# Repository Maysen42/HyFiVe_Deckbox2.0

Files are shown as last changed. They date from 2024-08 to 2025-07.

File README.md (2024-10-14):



# HyFiVe - Hydrography on Fishing Vessels

<figure> 
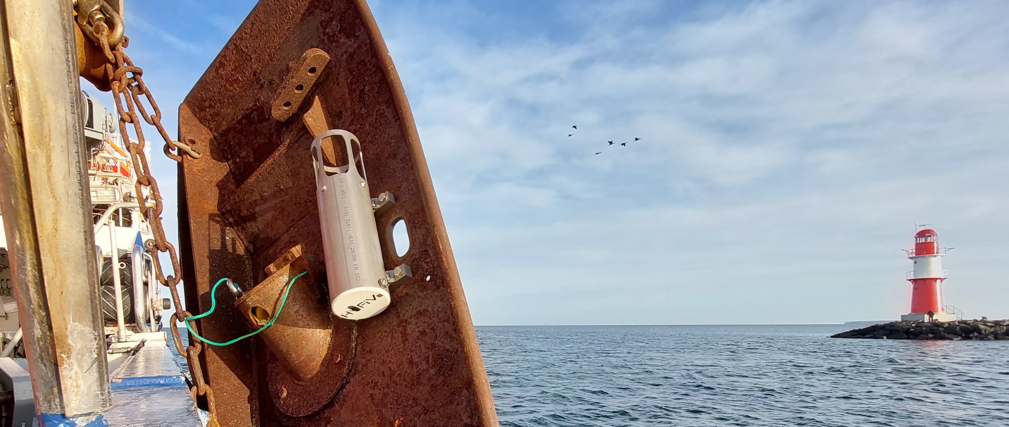
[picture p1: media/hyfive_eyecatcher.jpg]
hyfive_eyecatcher
   
</figure>

## Project Background 
Whether for modelling climate change or for our understanding of fish stocks – ocean data is essential for many disciplines. Usually, this data is collected by research vessels, which are cost-intensive and thus limited in space and time. To increase data resolution ‘vessels of opportunity’ can be a scalable alternative. In this concept vessels are used as measuring platforms, that are originally financed for a non-scientific purpose. Especially fishing vessels are of interest as they deploy gear in deep water and so make the whole water column accessible for an attached measuring system.

For this use case we developed a very flexible autonomous measuring system, which can be deployed on fishing gear to collect data in an affordable and scalable way. This was done within the **project ‘Hydrography on Fishing Vessels - HyFiVe’**
- Project period: Sept 2021 until Sept 2024
- Project partners:  
    - Thünen-Institute of Baltic Sea Fisheries (TIOF), Rostock, Germany, [https://www.thuenen.de/en/institutes/baltic-sea-fisheries/projects/fisheries-and-survey-technology/hyfive-hydrography-on-fishing-vessels](https://www.thuenen.de/en/institutes/baltic-sea-fisheries/projects/fisheries-and-survey-technology/hyfive-hydrography-on-fishing-vessels)
    - Leibnitz-Institute for Baltic Sea Research Warnemünde (IOW), Germany [https://www.io-warnemuende.de/project/278/hyfive.html](https://www.io-warnemuende.de/project/278/hyfive.html)
    - Hensel Elektronik GmbH, Rostock, Germany [https://hensel-elektronik.de](https://hensel-elektronik.de)
- Project webpage: hyfive.info
- Contact: See hyfive.info

## The HyFiVe System

This measuring system essentially consists of three components: 
- [01 Logger](./01_Logger/): Measures data with implemented OEM sensors while in the water and transmits them wireless afterwards.
- [02 Deck box](./02_Deckbox/): Receives measuring data via wifi, geo-references and stores it, visualizes it locally via webservice and transmits it to shore. The deck box also forwards config updates from server to loggers.
- [03 Land-Based Server](./03_Server/): Central infrastructure with a relational database, a configuration interface for remote maintenance and a tool for visualization of measuring data.

As overarching topic, [bi-directional communication](./bi_directional_communication/) between these components is described separately. 

The HyFiVe system offers many advantages:
- Autonomous operation up to several month
- Usable for non-experts, robust design
- Affordable price 
- Near live transmission of geo-referenced data to shore
- Scalability: Designed for a growing fleet of loggers and deck boxes
- Flexibility: Tested in various use cases, e.g. on trawl nets, as handheld probe and on sailing vessels 
- Modular design of logger facilitating easy change of sensors and integration of new ones
- Bi-directional data flow offering possibilities for remote servicing (VPN to deck box, config.json file for logger) 
- Comprehensive meta data
- Use of open sub-components and open standards lowering costs and facilitating reuse (e.g. ESP32, Raspberry Pi, nodeRed, InfluxDB, netcdf, https://cfconventions.org/ for naming variables)
- Open source, so you can modify and commercialise (according to the licenses below)

The system was developed in an agile method, so prototypes were built from an early stage on and tested continuously. Till the end of the first project in Sept 2024 the system was deployed on over ten vessels, among them research vessels, trawl fishing vessels, gill net fishing vessels and recreational vessels like sailing boats. 

<figure> 
   system_overview

   <figurecaption><a name="figure1">*Figure 1:*</a> *Logger, deck box and server - the three components of the HyFiVe measuring system*</figurecaption>
</figure>

## Github Repository
This documentation is aimed to enable you to build an own HyFiVe system and therefore contains detailed informations about all parts. If you are interested in building a system and lack information, please get in contact with us. 

**Disclaimer: We do not guarantee that the description is accurate throughout or complete. All your work is done at your own risk. Please comply with all necessary and legal safety precautions, especially when high voltage is involved, to avoid damage to yourself, others and the hardware.**

The three components have separate folders with hardware, software and specific information including READMEs which can be followed step by step. The READMEs contain
- Purpose and short description
- Used tools (hardware and software)
- Bills of Materials
- Additional information in the making/deploying

## Licenses
HyFiVe is an open-source project consisting of software, hardware, and documentation components. Each part of this project is licensed under a different copyleft license to ensure it remains free and open:

- Software/Code is licensed under [MPL-2.0](LICENSE_MPL-2.0)
- Hardware is licensed under [CERN-OHL-W-2.0 or later](LICENSE_CERN-OHL-W-2.0)
- Documentation is licensed under [CC-BY-SA-4.0](LICENSE_CC-BY-SA-4.0)

The HyFiVe logo is not published under above licenses and not free to use. 

An overview of the legal implications resulting from this licenses can be fund under [https://joinup.ec.europa.eu/collection/eupl/solution/joinup-licensing-assistant/jla-find-and-compare-software-licenses](https://joinup.ec.europa.eu/collection/eupl/solution/joinup-licensing-assistant/jla-find-and-compare-software-licenses).

## Funding
This project was funded by the German Federal Ministry of Food and Agriculture. 
<figure> 
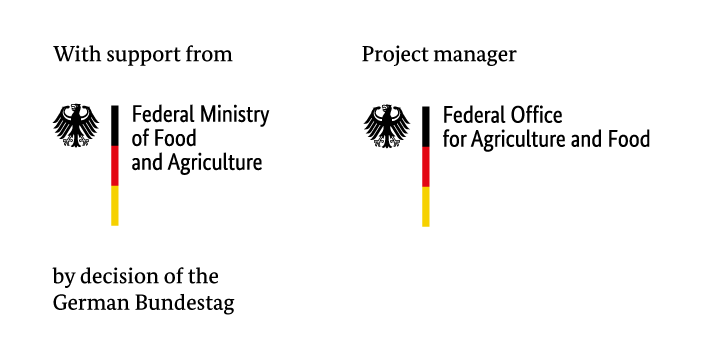
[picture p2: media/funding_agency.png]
funding_agency
   
</figure>

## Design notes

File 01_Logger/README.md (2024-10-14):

# Logger

The HyFiVe logger is an autonomous measuring unit, which can be attached to fishing gear. It consists of a pressure housing, internal electronics and firmware as well as sensors. 

Sensors: We integrate third-party (OEM) sensors. We are not limited to specific measurement parameters or manufactures. Many different sensors can be integrated, so the system can be adapted to your use case. So far we implemented and tested thoroughly sensors for conductivity, temperature, pressure (CTD) and oxygen.

Measurement process: The logger checks regularly if it is immersed into water. When the beginning of a deployment is detected, the state of logger is changed and it starts measuring with a prescribed period. When the logger is above the water surface again, this is also detected and the logger transmits the data via Wifi MQTT to the deck box. 

Config update: The configuration of the logger can be changed by altering config parameters, which are contained in a config.json file. The logger tries in regular intervals (which are also a config parameter) to connect to the deck box and asks, if a new config is available for it. If so, it is transmitted via Wifi MQTT.

## Different Versions of HyFiVe Loggers

We developed two versions of HyFiVe loggers. The HyFiVe deck box and the server do not need to be adapted to the logger version, they work with both.

There is no significant difference between the two versions regarding: 
- Mechanics (Only one end cap and the internal mountings are different)
- Sensors

The main differences between both versions are explained below. Both versions are explained in detail in the corresponding subfolders. 

### Basic Logger
The [basic logger](./01_Basic_Logger/) was developed by building prototypes from an early stage on (agile development). The prototypes were deployed in field tests and the results used to improve the design. Until the end of the first HyFiVe project in Sept 2024, all measuring campaigns on more than 10 vessels were conducted with this logger version. 

The electronic design is straight forward and easier to reproduce than the modular logger. It is based on only one PCB. All sensors are directly interfaced to micro controller on the PCB. 

<figure> 
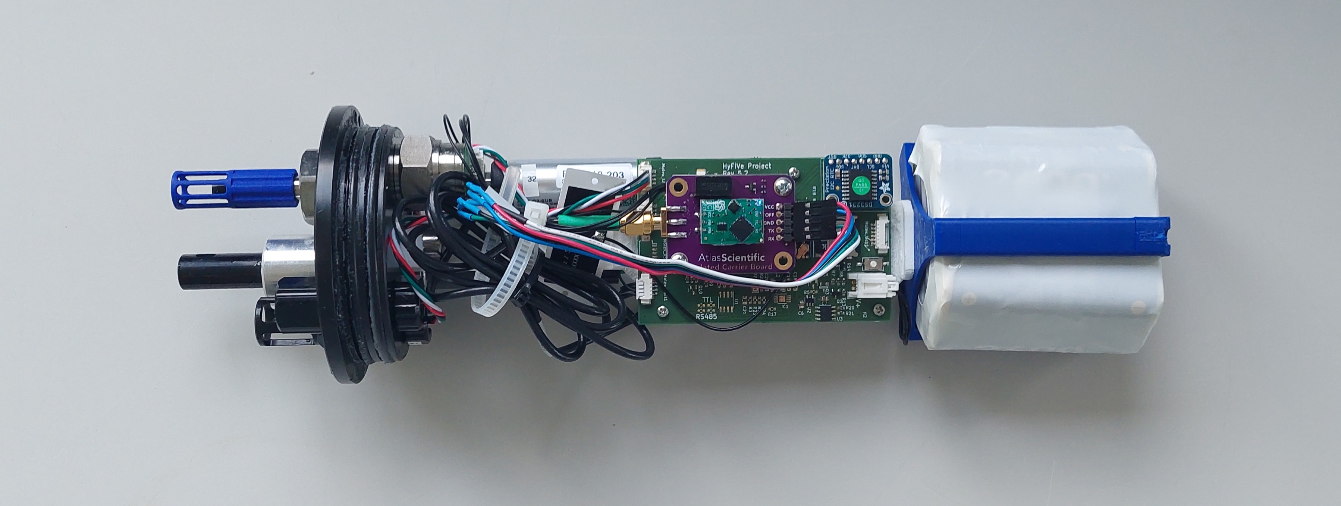
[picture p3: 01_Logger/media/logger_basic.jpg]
basic_logger
   

   <figurecaption><a name="figure1">*Figure 1:*</a> *Electronics of basic logger*</figurecaption>
</figure>

### Modular Logger
The [modular logger](./02_Modular_Logger/) offers more functionalities and it's design is more complex. The development took more time, so the prototypes could only be tested in harbour tests until the end of the first HyFiVe project in Sept 2024. 

The modularity is the main difference between both versions: In the modular logger each sensor is connected to one interface PCB. All interface PCBs are connected to a main PCB. The communication between main PCB and interface PCB is standardized. In this way, all sensor specific things can be encapsulated on the interface PCB.

In comparison to the basic version, the modular logger offers the following additional features: 
 - Modular design facilitates integrating and changing sensors, s. above.
 - Battery management
 - Charging of batteries without opening pressure case 
 - LED for feedback
 - Magnetic switch, e.g. for resetting the logger
 - Easier update of logger configuration: Manual trigger of update with magnet possible, more config parameters available, more precautions taken for stable config update
 - Error Log
 - Special operation modes possible: Change of sample rate for single sensors or during down- and upcast
 
<figure> 
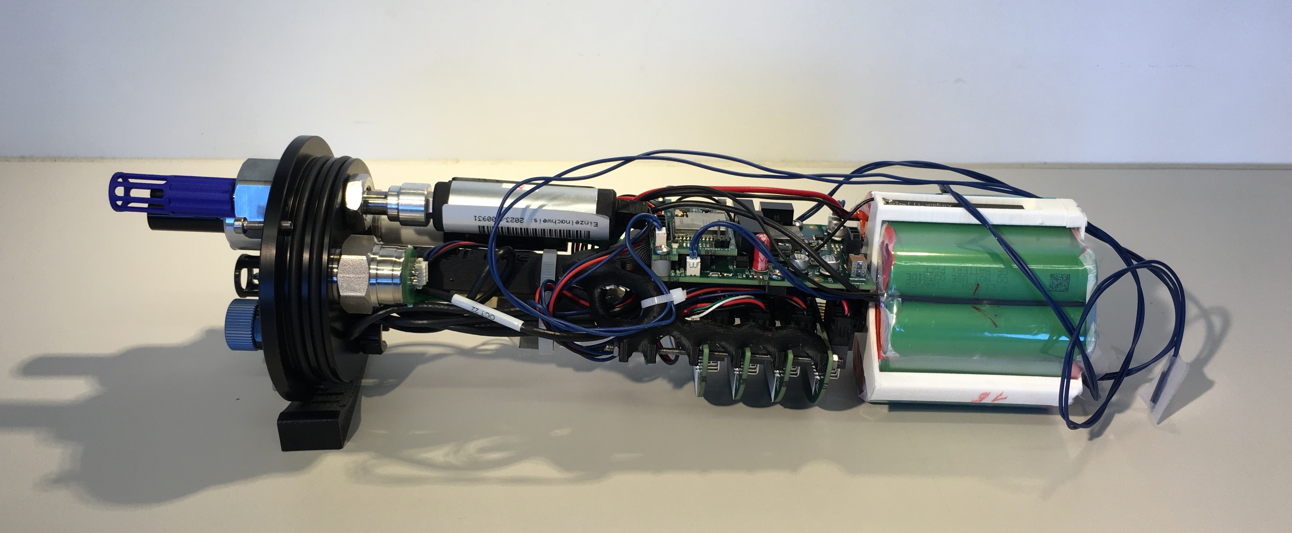
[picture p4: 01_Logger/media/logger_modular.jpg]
modular_logger
   

   <figurecaption><a name="figure2">*Figure 2:*</a> *Electronics of modular logger*</figurecaption>
</figure>

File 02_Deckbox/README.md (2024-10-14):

# Deck box

<figure> 
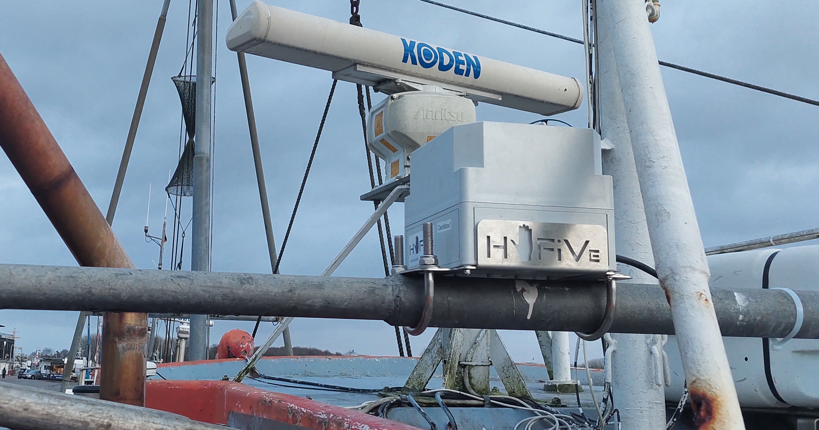
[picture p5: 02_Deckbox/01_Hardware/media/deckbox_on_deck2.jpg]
deckbox_on_deck
   

   <figurecaption><a name="figure1">*Figure 1:*</a> *Deck box installed on mast of fishing vessel using steel mounting*</figurecaption>
</figure>

## Main Components

The main hardware components of the deck box are:
- Router RUT955 by Teltonika
- Raspberry Pi 4B
- power supply and antennas
- waterproof case incl. internal and external mounting

## Main Functionalities 
The router provides:
- Wifi incl. MQTT broker for communication to the logger
- Mobile internet connection for communication to server
- GPS, published as NMEA string
- NTP server for time update of logger
- VPN client incl. port forwarding to Pi for remote servicing of deck box

The Raspberry Pi runs the main functionalities of the deck box:
- InfluxDB: Timeseries database for storing measuring data locally and buffering GPS data
- NodeRED: Handling all data flows:
    - measuring data is received via MQTT, merged with GPS data and stored locally
    - measuring data is saved as netCDF file and send to server in regular intervals
    - status files are received from loggers and forwarded to server
    - config files are downloaded from server in regular intervals
    - config files are send via MQTT, if requested by logger (incl. writing an error log)
- Grafana: Webinterface available for crew on board to visualize measuring data offline
- Self developed visualization webinterface (by a student): Installation is described, but files not contained in this repo, see [https://github.com/TreeM4n/HyFiVe](https://github.com/TreeM4n/HyFiVe)
- Docker and Portainer: Used for encapsuling above software

## Instructions

To build and configure a deck box follow the instructions in the following chapters:
1. [**Hardware:**](./01_Hardware/) Description of the mechanic and electric hardware incl. Bills of Material.
2. [**Software:**](./02_Software/) Description of the software setup.

<figure> 
   whole_deckbox_named

   <figurecaption><a name="figure2">*Figure 2:*</a> *Look inside a deck box*</figurecaption>
</figure>

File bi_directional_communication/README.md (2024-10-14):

# Bi-directional Communication between Server and Logger

## Data Flow from Logger to Server

<figure> 
   Data_flow_logger2land

   <figurecaption><a name="figure1">*Figure 1:*</a> *Data flow from logger to land*</figurecaption>
</figure>

The following data flow on the server is described in [../03_Server](../03_Server/)

This flow consists mainly of **measuring data**:
1. After a deployment, the logger tries to connect with the Wifi and send the data via MQTT
2. On the deck box in  NodeRED the data is merged with buffered GPS info and saved locally to the Influx database.
3. In regular intervals NodeRED triggers a python script, which aggregates new deployments into netCDF files, and sends them via sftp to the server (mailbox/in/netcdf/logger_ID/).
4. On the server, the measuring data is quality checked and saved in the relational data base
5. The measuring data is forwarded to other data bases via interfaces and can be visualised on our own [web interface](../03_Server/04_Webinterfaces/) under hyfive.info:4001

In addition each logger sends **status information**:
1. Each logger sends in regular intervals (which is a config parameter) it's battery and memory status via Wifi/MQTT.
2. On the deck box in NodeRED this information is merged with the current position of the deck box and saved as a status.json file
3. This file is sent via mobile network and sftp to the server (mailbox/in/status/logger_ID/). Example file: [logger_17_status_1724931613709.json](./logger_17_status_1724931613709.json)
4. The information is shown in the config [interface](../03_Server/04_Webinterfaces/).

## Data Flow from Server to Logger

<figure> 
   Data_flow_land2logger

   <figurecaption><a name="figure2">*Figure 2:*</a> *Data flow from land to logger*</figurecaption>
</figure>

An aim of the HyFiVe project is, that a fleet of measuring systems can be managed with small effort. Therefore we developed a ways of remote servicing.

A comprehensive way for remote servicing the deck box, is to connect to it via VPN. The expert user onshore can configure both main components, the router (via it's webinterface) and Raspberry Pi (via SSH). Also all software interfaces like NodeRED and InfluxDB can be reached via port forwarding. 

For changing the configuration of loggers, which are already deployed on a remote vessel, we defined a set of config parameters, which are stored in a config.json file.

The **config files** can be created with an [web interface](../03_Server/04_Webinterfaces/) on the server and handed down from server to loggers:
1. Creation:  
After creation by the webinterface, the config files are stored on the server:
    - location: mailbox/out/config/logger_ID/
    - file name: logger_ID_config_DATE, with DATE like YYYYMMDDHHMM, e.g. logger_10_config_202405071357
The format of the file name is important and shall not be altered, as the ID in the file name is used to them assign to the right logger and the date is used to identify the latest file. 
2. Transmission from server to deck box:   
Each deck box copies all config files from the server to a local repository. This is done in regular intervals by a flow in NodeRED on the deck box. 
3. Transmission from deck box to logger:  
As a deck box does not know which loggers are close and also has no way (implemented) to start a MQTT connection, the loggers need to ask for updates. They do this in regular intervals given by the config parameter config_update_periode. The process is described in detail below. 

More info on config parameters and their transmission is given in [./01_config_update/](./01_config_update/).

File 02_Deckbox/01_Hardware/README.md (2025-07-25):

# Bill of material

The following parts are needed to manufacture a HyFiVe deckbox.

| #   | Amount | Unit | Name                                                                                                                        | GTIN                                  |
| --- | ------ | ---- | --------------------------------------------------------------------------------------------------------------------------- | ------------------------------------- |
|     |        |      | **Electronic components**                                                                                                   |                                       |
| 1   | 1      | pc   | Raspberry Pi 4 B 4GB ram , incl. Micro SD card (min 8 GB) and official case                                                 | 0765756931182  644824914923           |
| 2   | 1      | pc   | Router Teltonika RUT955 incl. supplied antennas (2 x wifi, 2 x mobile data, 1 x GPS)                                        | 4779027311302                         |
| 3   | 1      | pc   | Sim card incl. mobile data                                                                                                  |                                       |
| 4   | 1      | pc   | Network cable, short, small bending radius (e.g. 0.2 m)                                                                     | e.g. 4052792024371                    |
|     |        |      | **Internal power supply**                                                                                                   |                                       |
| 5   | 1      | pc   | Self designed PCB  for power distribution incl. fuse and diodes, see (TODO **LINK TO SCHEMATICS**)                          | self manufactured                     |
| 6   | 1      | pc   | ACDC converter, 12 or 24 V output, min 20 W, e.g. Mean Well LPV-20-12 LED Trafo                                             | 4021087006965                         |
| 7   | 1      | pc   | DCDC Converter, Input 8-58V, output: 5V, max. 15 W, e.g. K480503                                                            | 8852090466622                         |
| 8   | 1      | pc   | power plug for RUT955, either cut and reused from ACDC unit                                                                 |                                       |
| 9   | 1      | pc   | alternativly: Molex crimp socket 'Micro-Fit' 2x2-poles plus 4 x crimp contact  2824-20                                      | product numbers 0039039042 430300038  |
| 10  | 2      | pc   | 2-core wire ~25 cm, 2 x ~0.5mm², red and black                                                                              | 4040849567070                         |
| 11  | 6      | pc   | electric wire ferrule 0.5mm² 												    | 9900000247027			    |
| 12  | 4      | pc   | Heat shrink tubing 20mm x 3mm 												    | 9900000174064			    |
| 13  | 1      | pc   | USB-C Plug, e.g. recable USB C to C plug 5 strands set (consits of 3 parts: plug, housing and heat shrink tubing)           |		  	                    |
|     |        |      | **External power supply**                                                                                                   |                                       |
| 14  | 1      | pc   | Power cable, ~15 m, 2 wires, ~1mm², suited for outdoor/deck                                                                 | 2050005621999                         |
|     |        |      | **For connection to 230  V**                                                                                                |                                       |
| 15  | 1      | pc   | Socket Weipu SP2212/P3-1N, male, 3 pins, IP68                                                                               | 2050001515001                         |
| 16  | 1      | pc   | Plug Weipu SP2110 / S 3 I, female, 3 pins, IP68                                                                             | 2050001514738                         |
| 17  | 1      | pc   | Cover Weipu SP2110-Cap                                                                                                      | 2050001515353                         |
| 18  | 1      | pc   | Cover Weipu SP2111-Cap                                                                                                      | 2050001515360                         |
| 19  | 1      | pc   | Protected contact plug (Schuko) for connection to 230 V grid                                                                | 4011160604126                         |
|     |        |      | **For connection to 12/24 V**                                                                                               |                                       |
| 20  | 1      | pc   | Socket Weipu SP2212/P2-1N, male, 2 pins, IP68                                                                               | 2050001514998                         |
| 21  | 1      | pc   | Plug Weipu SP2110 / S 2 I, female, 2 pins, IP68                                                                             | 2050001514721                         |
| 22  | 1      | pc   | Cover Weipu SP2110-Cap                                                                                                      | 2050001515353                         |
| 23  | 1      | pc   | Cover Weipu SP2111-Cap                                                                                                      | 2050001515360                         |
| 24  | 1      | pc   | Plug of your coice for connection to low voltage grid                                                                       |                                       |
|     |        |      | **Case incl. internal mountings**                                                                                           |                                       |
| 25  | 1      | pc   | FIBOX Case 180x180x150 (Product-No.: 6011323)                                                                               | 6418074052216                         |
| 26  | 1      | pc   | 3D printed mounting for electronic components, consisting of four parts TODO **Link to STEP files**                         | self manufactured                     |
| 27  | 1      | pc   | 3D printed mounting for antennas of RUT955, consisting of three layers<br>TODO **Link to STEP files**                       | self manufactured                     |
| 28  | 4      | pc   | Threaded inserts to melt into 3D print, M3x5x4                                                                              | e.g. ASIN B09B7F2XM3 or 4260528721160 |
| 29  | 4      | pc   | Allen screws M3x16                                                                                                          | 4043952175507                         |
| 30  | 2      | pc   | Cable ties small                                                                                                            | 9900000247645                         |
| 31  | 2      | pc   | Tapping screw 2.2 x 6.5                                                                                                     | 4043377162199                         |
| 32  | 28     | pc   | Tapping screw 2.9 x 9.5                                                                                                     | 4043952537589                         |
| 33  | 4      | pc   | Tapping screw 3.9 x 9.5                                                                                                     | 4043377159625                         |
| 34  | 4      | pc   | (plastic) washers for 3.9 mm with large outer diameter                                                                      | 4043952665589 or 4001796381737        |
| 35  | 1      | pc   | ~5 cm foam tape (20 x 2 mm)                                                                                                 | 4260396830346                         |
|     |        |      | **Mounting for box on reeling**                                                                                             |                                       |
| 36  | 1      | pc   | Mounting plate, watercutted, stainless steel V4A<br>TODO **Link to STEP files**                                             | self manufactured                     |
| 37  | 4      | pc   | Allen screw, M4x16, incl. washer and self-securing nut, stainless steel V4A                                                 | 4043377065032			    |
| 38  | 2      | pc   | Steel strap for tubes, DIN 3570, nominal width 46 mm, incl. 2 M10 self-securing nuts and 2 M10 washers, stainless steel V4A | 4043952396568                         |
| 39  | 2      | pc   | Steel strap for tubes, DIN 3570, nominal width 82 mm, incl. 2 M12 self-securing nuts and 2 M12 washers, stainless steel V4A | 4043377302007                         |

# Needed tools

- Drilling machines 22 mm holes
- Soldering station, including equipment
- Adapter tip for melting in press nuts
- Tweezers
- Diagonal pliers
- flat nose pliers
- wire stripper
- Heat gun
- Wrench 27 mm
- Allen wrench 2.5 and 3 mm
- Screwdriver PH1 + PH2
- Screwdriver flathead (2.5)
- Caliper
- Sikaflex (e.g. 291i  or some other marine certified adhesive sealant)
- Spatula
- Crimp-Tools for 2824-20 and for electric wire ferrules
- Cleaning equipment: ethanol, q-tips, lint-free wipes

# Self manufactured components

The following components need to be manufactured according to design files provided in this Github repository:
- PCB for power distribution: 
   - Both power inputs of the deckbox (DC and AC) are fed into this PCB (AC after converting to DC). The PCB holds a fuse and two diodes for backflow protection. So both power inputs can be connected at the same time without damage, and also both inputs are fed through the fuse. 
   - The function of the PCB is also depicted in the [flow diagram below](#connect-components)
   - To reproduce the PCB, you find all necessary infos in the subfolder [./02_electronic/PCB_DC_PowerDistrubution/](./02_electronic/PCB_DC_PowerDistrubution/). Order the PCB at a manufacturer of your choice and fit the parts included in the Bill of Material.
     TODO **Update PCB Schematics with bigger clams for Cables with "Aderendhülsen"**
- 3D printed mountings: Use a 3D printer to manufacture 1 x mounting for antennas (consisting of 3 subcomponents called levels) and 1 x mounting for electronic parts (consisting of 4 subcomponents). Use the stl files provided in [./01_mechanic/01_internal_mounting/](./01_mechanic/01_internal_mounting/). Printer settings can be chosen as you like (we used ABS, 20% infill, fast mode on an Ultimaker S5). TODO **Check Subcomponents! Are Settings still up to date?** 
- Water-cut mounting: If you want to mount the deckbox on a reeling, you can use a water-cut mounting plate as shown in the picture below. You can use the step file provided in [./01_mechanic/02_external_mounting/](./01_mechanic/02_external_mounting/) and order at a manufacturer of your choice (price approx. 60 €). 

<figure> 
   deckbox_on_deck
</figure>

# Assembly
## Deckbox top
### Antenna mount (top level)
- Insert Wi-Fi and mobile antennas into the holder. The same antennas should be orthogonal to each other.
- The antenna should click when it is locked into the bracket.
- Guide the cables through the corresponding slots

<table>
  <tr>
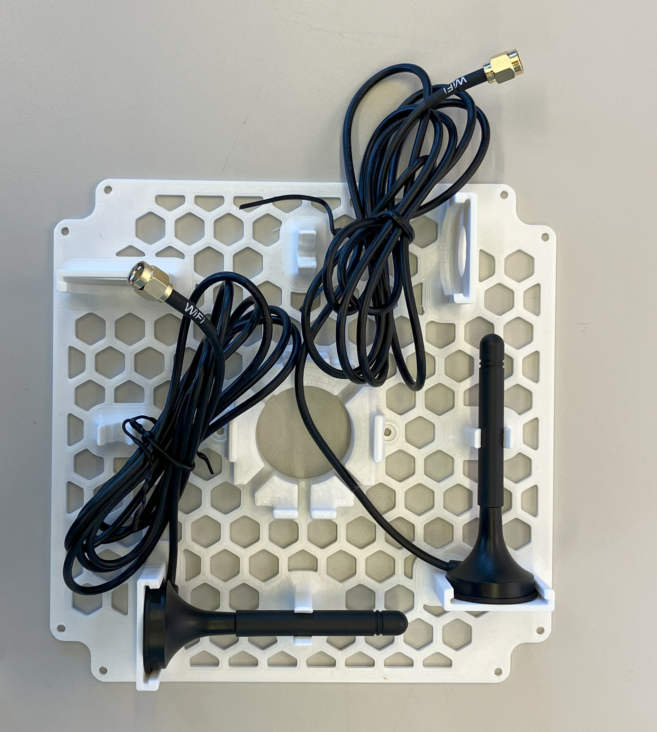
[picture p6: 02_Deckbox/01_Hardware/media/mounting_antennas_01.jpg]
    <td></td>
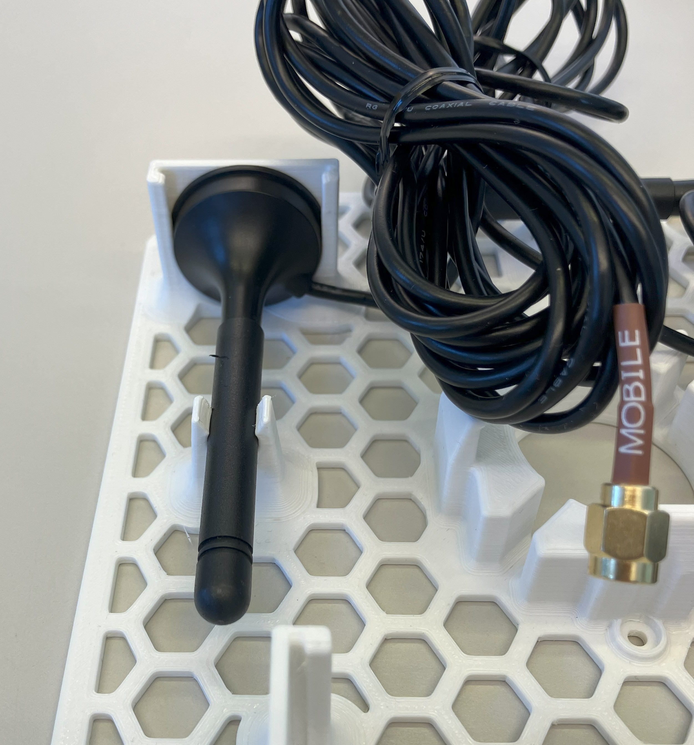
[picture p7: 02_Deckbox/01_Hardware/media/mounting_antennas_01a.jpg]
    <td></td>
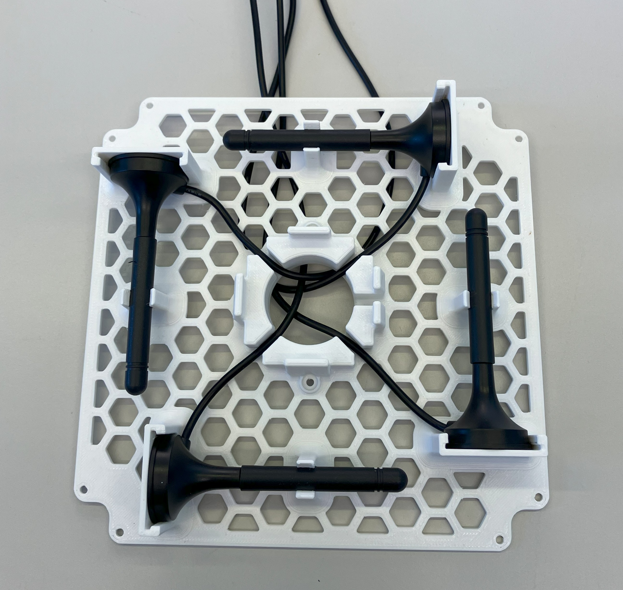
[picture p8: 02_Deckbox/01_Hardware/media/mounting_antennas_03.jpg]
    <td></td>
  </tr>
</table>

- Guide the GPS antenna cable and click the antenna into place.
<figure> 
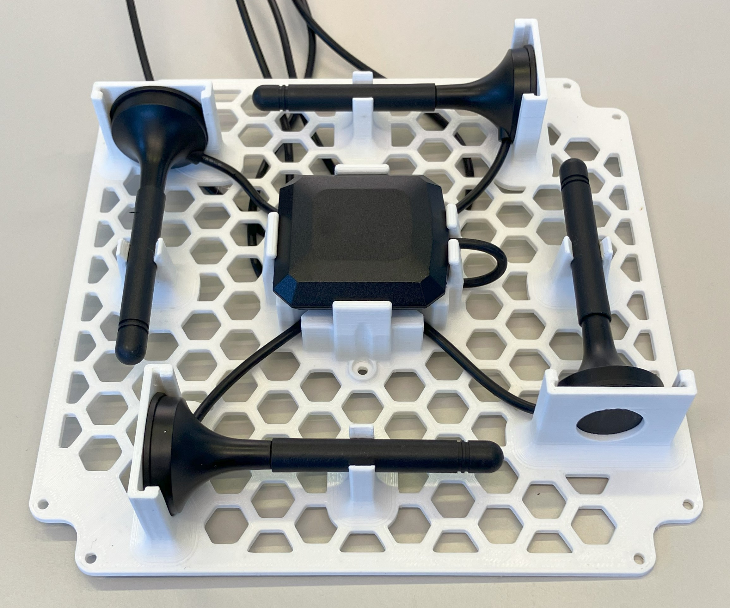
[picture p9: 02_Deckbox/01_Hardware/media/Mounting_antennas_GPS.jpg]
GPS Antenna
   
</figure>

### Antenna mount (middle level)
- Insert the middle level of the antenna mount and guide all 5 cables through.

<figure> 
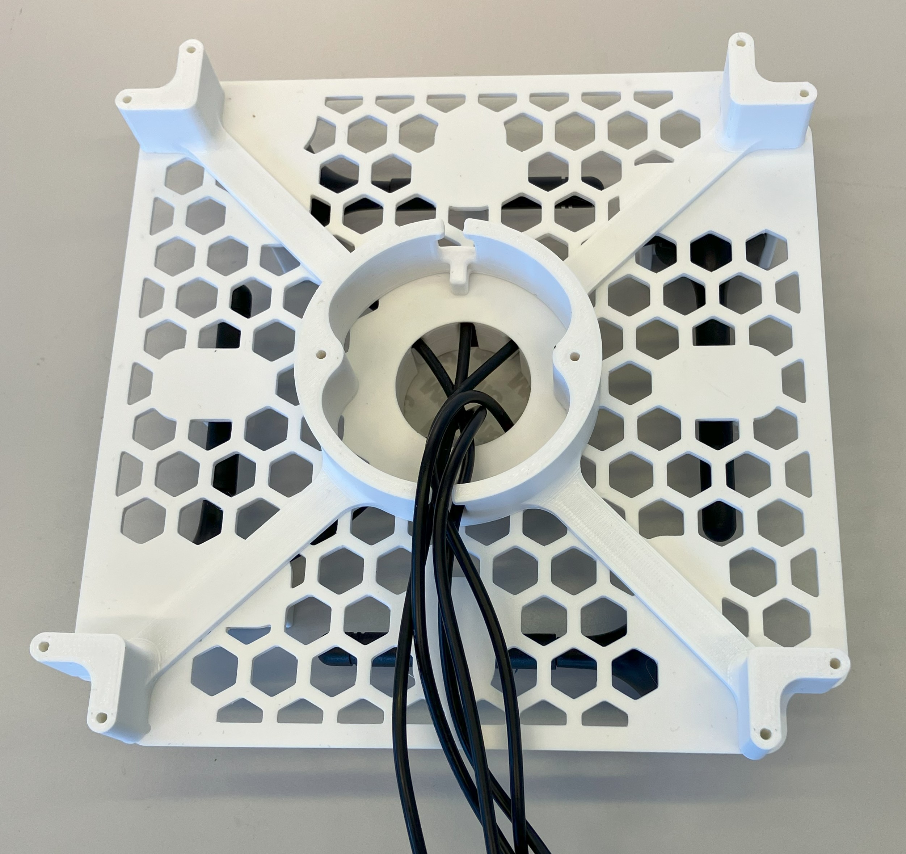
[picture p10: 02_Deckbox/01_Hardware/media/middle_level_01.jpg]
middle level
   
</figure>

- Screw the top and middle levels together using 10 metal screws (2.9 x 9.5) starting from the center and then the corners.

<table>
  <tr>
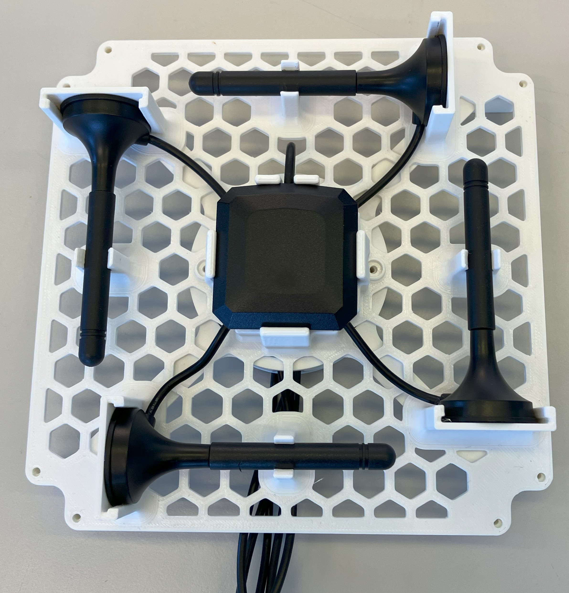
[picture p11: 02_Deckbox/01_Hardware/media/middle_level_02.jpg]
    <td></td>
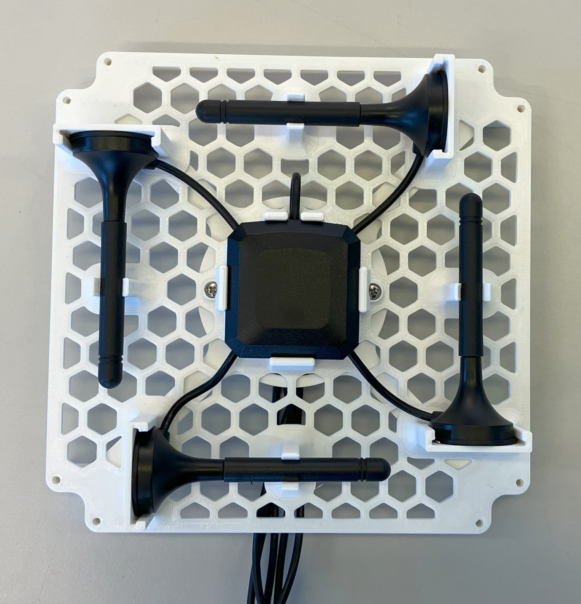
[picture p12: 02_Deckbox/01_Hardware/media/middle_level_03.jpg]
    <td></td>
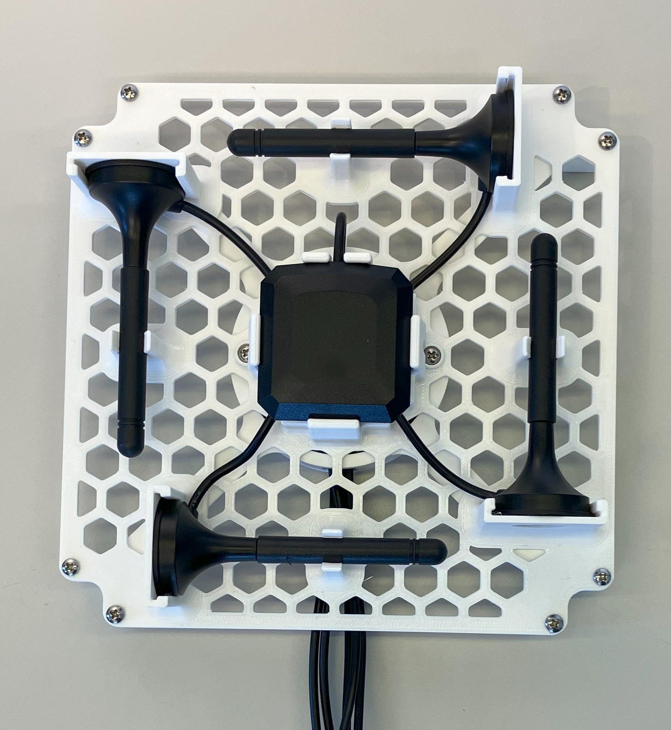
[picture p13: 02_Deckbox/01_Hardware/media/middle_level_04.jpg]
    <td></td>
  </tr>
</table>

- Bundle the cables with cable ties (2.5mm) and attach them to the middle level

<figure> 
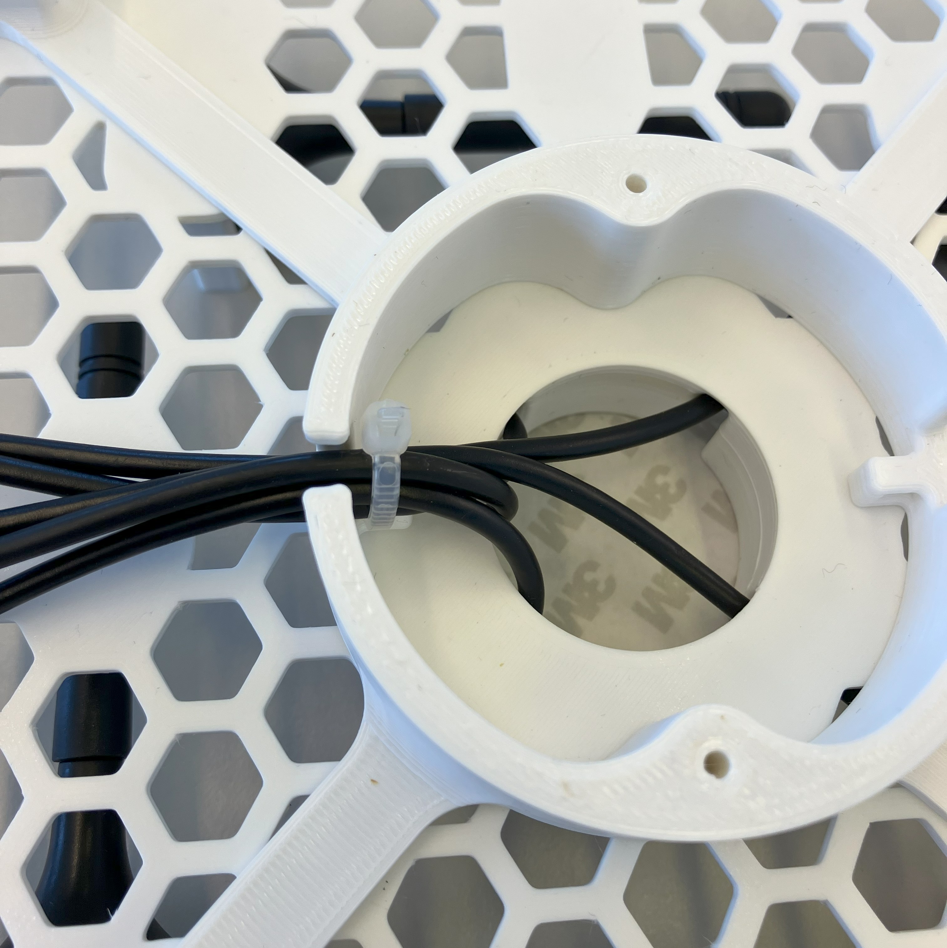
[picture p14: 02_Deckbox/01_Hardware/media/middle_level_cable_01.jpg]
middle level cable
   
</figure>

- Wind the cables together at the middle level, leaving 30 cm of each cable loose, and guide them back through the second opening (Note: Wi-Fi cables are shorter than the others!). It is recommended to keep the winding flat so that the cables can be easily guided back.
- Bundle the cables again and secure them with cable ties

<table>
  <tr>
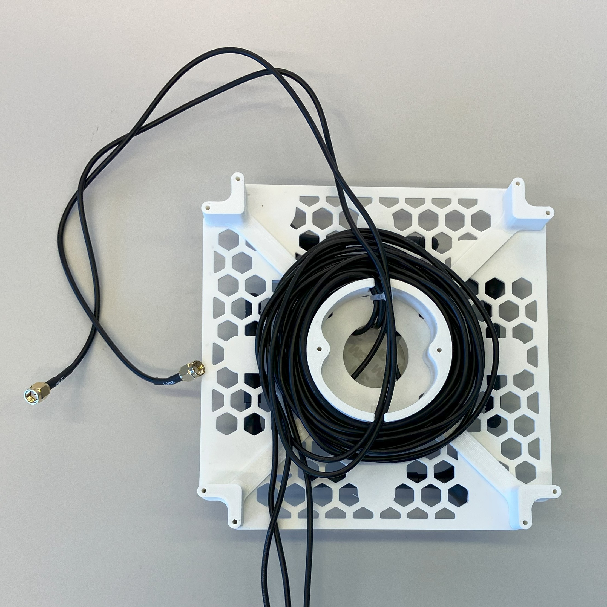
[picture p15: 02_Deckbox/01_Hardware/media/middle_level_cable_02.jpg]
    <td></td>
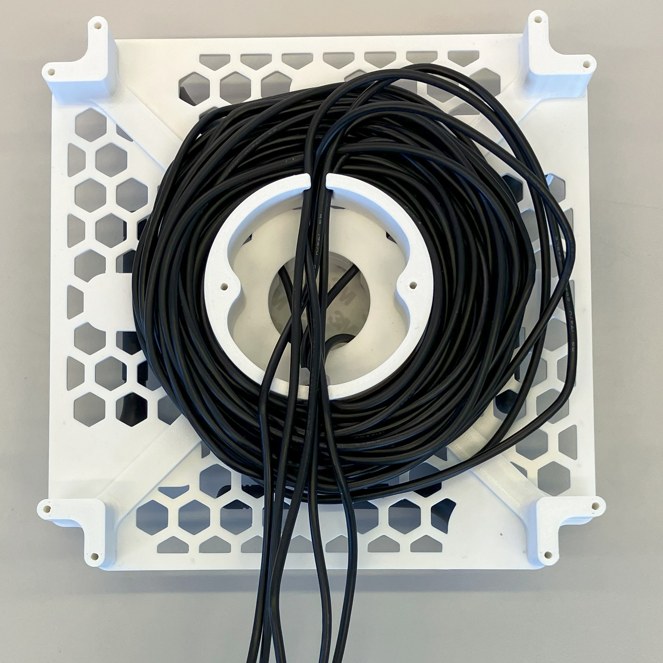
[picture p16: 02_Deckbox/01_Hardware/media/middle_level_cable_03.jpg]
    <td></td>
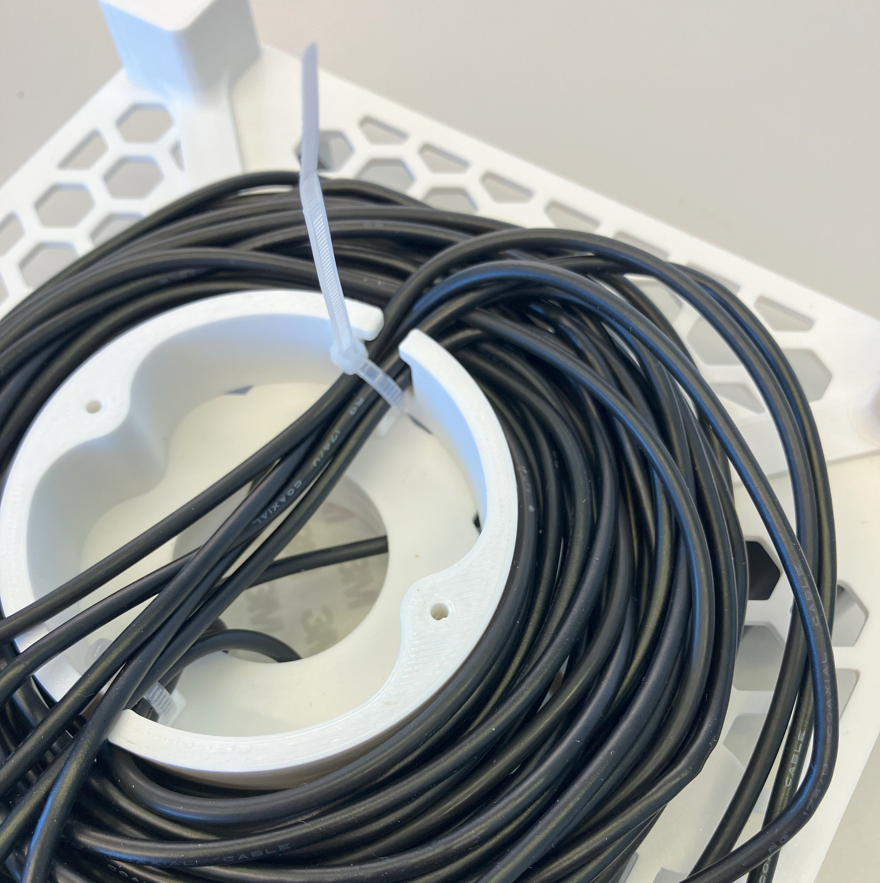
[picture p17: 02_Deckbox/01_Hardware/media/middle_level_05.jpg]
    <td></td>
  </tr>
</table>

### Antenna mount (bottom level)
- Using a soldering iron and an M3 adapter tip at approximately 180°C, melt the threaded inserts into the corners of the bottom level.
- If necessary, first free the hole by screwing in an M3 cylinder head screw.

<figure> 
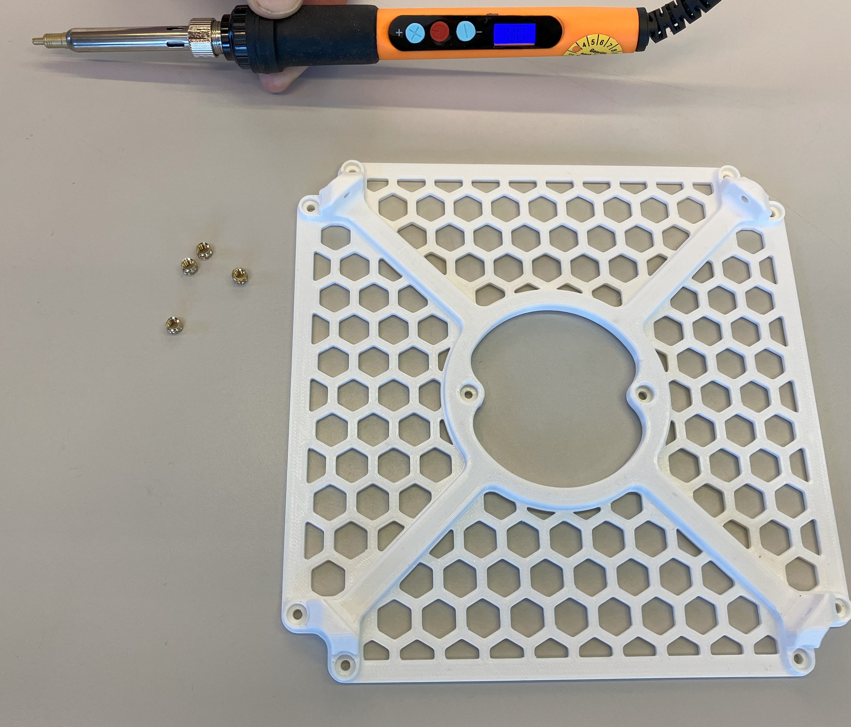
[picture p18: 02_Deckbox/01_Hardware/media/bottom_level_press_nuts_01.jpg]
requirements for bottom level
   
</figure>

- Place a threaded insert on the soldering iron with tweezers (**Attention: Hot!**).

<table>
  <tr>
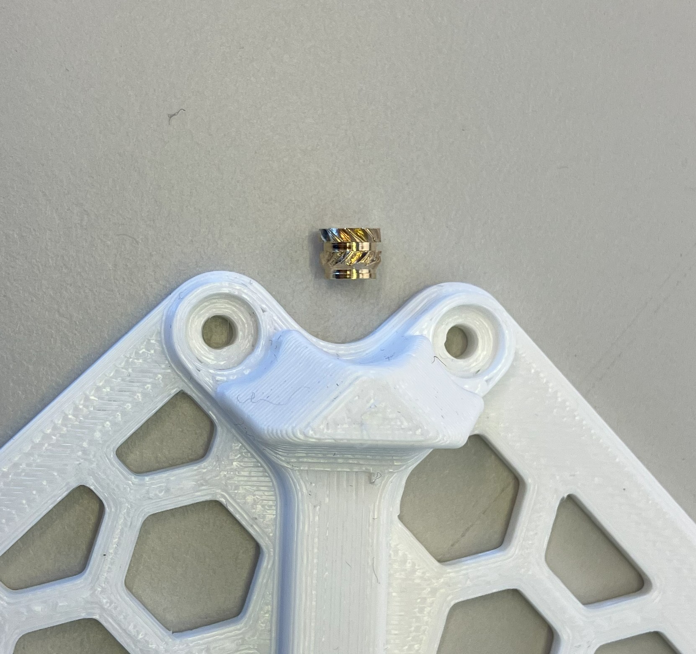
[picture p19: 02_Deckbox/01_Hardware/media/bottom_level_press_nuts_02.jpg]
    <td></td>
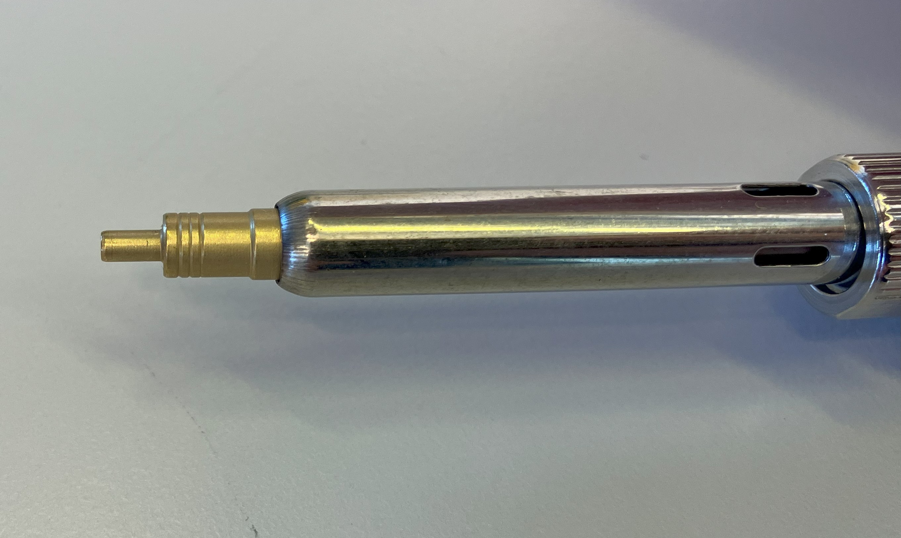
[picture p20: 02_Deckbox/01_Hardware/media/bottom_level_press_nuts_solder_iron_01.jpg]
    <td></td>
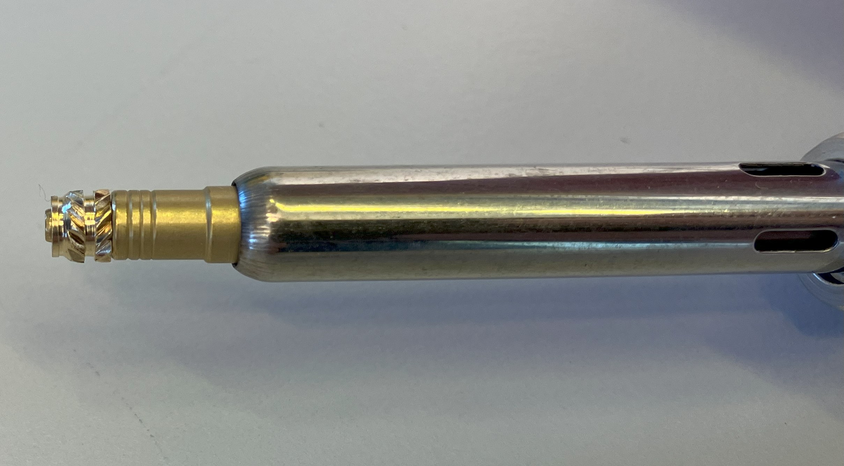
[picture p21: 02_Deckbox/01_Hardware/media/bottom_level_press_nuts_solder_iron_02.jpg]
    <td></td>
  </tr>
</table>

- Melt in the threaded insert

<table>
  <tr>
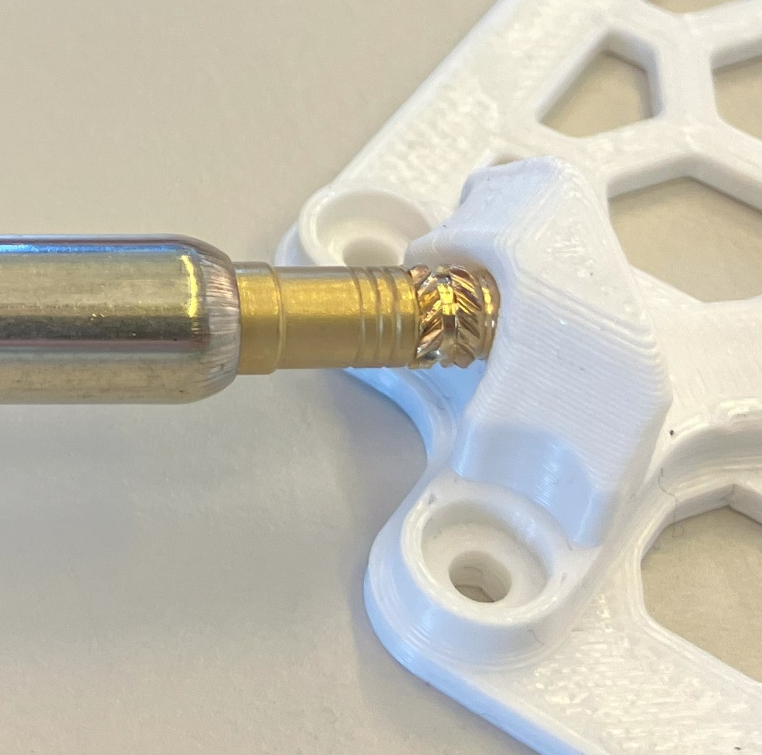
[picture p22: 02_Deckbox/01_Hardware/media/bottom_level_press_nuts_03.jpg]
    <td></td>
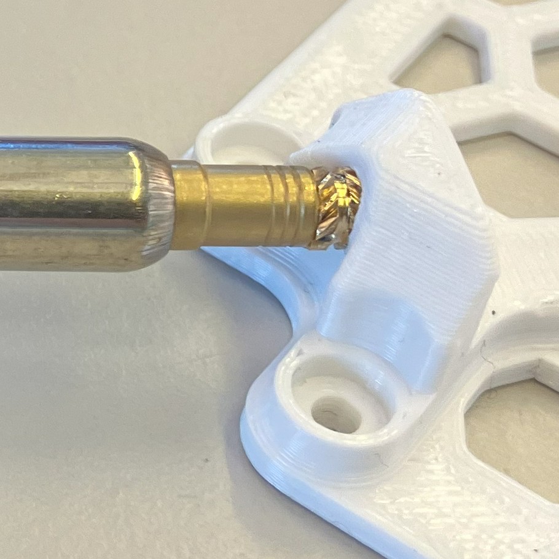
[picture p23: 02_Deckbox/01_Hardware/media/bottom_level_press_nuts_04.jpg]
    <td></td>
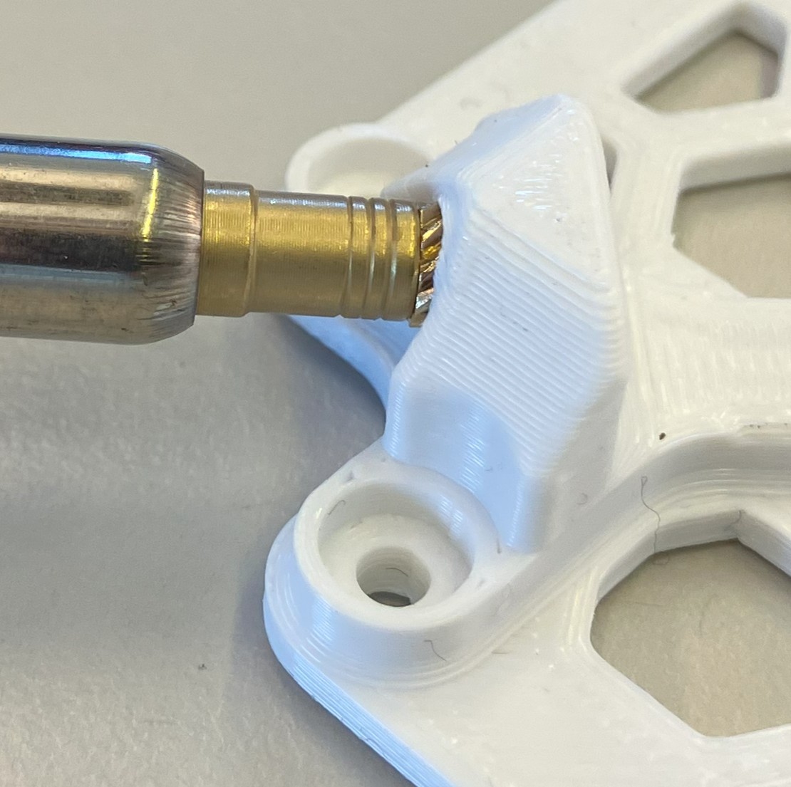
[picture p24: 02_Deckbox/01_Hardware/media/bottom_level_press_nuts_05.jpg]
    <td></td>
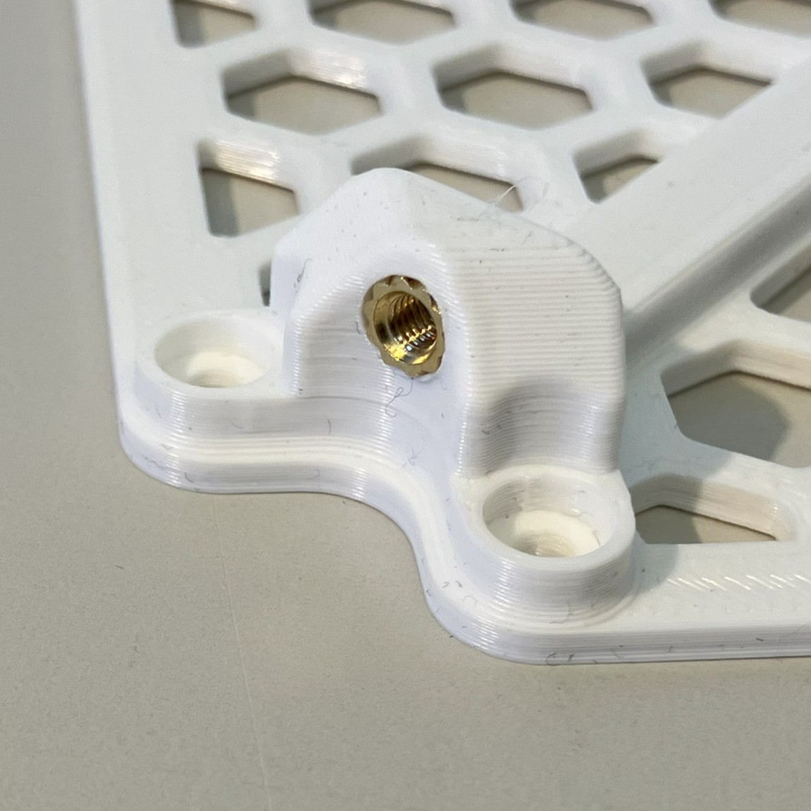
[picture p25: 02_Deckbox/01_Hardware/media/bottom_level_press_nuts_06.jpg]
    <td></td>
  </tr>
</table>

- Repeat the melting process on all 4 corners.
- For later attachment to the deckbox lid, screw 4 cylinder head screws from the inside into the threads.

<figure> 
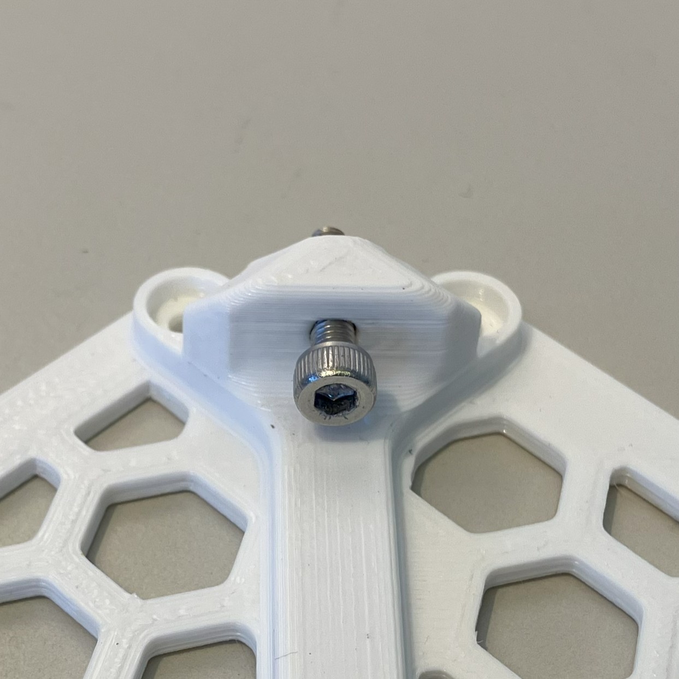
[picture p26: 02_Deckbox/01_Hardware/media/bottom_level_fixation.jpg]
screws in nuts
   
</figure>

- Guide the cables through the middle opening of the bottom level and place them on the middle level.
- Screw the bottom level into place using 10 metal screws, similar to the top level.
- Place the entire mount in the deckbox lid and secure it with screws in the corners.

<table>
  <tr>
    <td></td>
    <td></td>
    <td></td>
  </tr>
</table>

---

## Mounting components to the deck box bottom
### Drill holes for the power supply
- Using a step drill, create a 22 mm hole on two opposing sides (centered, 25 mm from the top edge).

<figure> 
   drawing for weipu sockets
</figure>

- Control the drilled holes

<figure> 
   control holes weipu sockets
</figure>

### Installing the Bottom Plate
- Insert the bottom plate into the deckbox, paying attention to the recess for the Weipu connectors.
- Secure the plate with 4 plastic washers and 4 metal screws (3.9 x 9.5).

<figure>
	</td>
</figure>

### AC/DC Converter
- Press the AC/DC converter into the housing.
<figure> 
   ACDC converter with holder
</figure>

- Screw the housing to the bottom plate with 2 metal screws (2.9 x 9.5mm) in the orientation as shown on the picture. 

<figure> 
   ACDC converter on bottom plate
</figure>

### PCB on AC/DC Housing
- Screw the PCB onto the AC/DC housing with 2 metal screws **(2.2 x 6.5 mm)**.\
**Attention: DO NOT confuse the screws with 9.5 mm length, otherwise the AC/DC-converter might take damage**

<figure> 
   PCB on ACDC housing
</figure>

### Connecting Weipu AC connector (3-Pole)
- Unscrew the nut and thread it onto the blue and brown cables of the AC/DC converter.
- Guide the cables outward through the hole.

<figure> 
   install weipu sockets 01
</figure>

- Shorten the AC cable to 10 cm from the deckbox and strip the insulation for about 6 mm.
- Remove the O-ring (seal) from the weipu socket, as it can not be used becaue the wall of the fibex case is to thick. The weipu socket will be glued in later.
- Put two shrink tubing on the wire, one on each core and solder the Weipu connector (3-pole) to the cable. The blue core has to be connected to pin 1 and the brown to pin 2 of the connector (it also works the other way around). Pin 3 (Ground) is not connected.
- Shrink the heat shrink tubing onto the pins, trying to have as little of the pin uncovered as possible.

<table>
  <tr>
    <td></td>
    <td></td>
  </tr>
</table>

### Connecting Weipu DC connector (2-Pole)
- Similar to AC-Connector, unscrew the nut and thread it onto the black and red cables. Guide the cables outward through the hole.
- Remove the O-ring (seal) from the weipu socket, as it can not be used becaue the wall of the fibex case is to thick. The weipu socket will be glued in later.
- Put two shrink tubing on the wire, one on each core and solder the Weipu connector to the cable. Black (ground) to pin 1 (at the top, marked whith a white dot) and red (lead) to pin 2 at the bottom of the connector.
- Shrink the heat shrink tubing onto the pins, trying to have as little of the pin uncovered as possible.
- Attach two electric wire ferrules on the other end of the wire.

<figure> 
   install weipu sockets 02
</figure>

### Glueing / Sealing Weipu connectors with Sikaflex
- Both weipu sockets needs to be glued in the fibexas the deckbox wall is too thick. Use Sikaflex for this purpose.
- Clean the surfaces of the deckbox and Weipu connector in the contact area with alcohol.
- Apply Sikaflex (291i) to the flange of the Weipu connector with a spatula (as sparingly as possible, but there should be a continuous film on the connector).

<table>
  <tr>
    <td></td>
    <td></td>
  </tr>
</table>

- Insert the connector (white dot pointing up) and screw it into place (27 mm wrench)
- Scrape off excess sealant with a q-tip

<figure> 
   install weipu sockets 02
</figure>

- Repeat the procedure with the second weipu connector. The result should look like on the following picture.

<figure> 
   install weipu sockets 02
</figure>

### Mounting the Raspberry Pi
- Cut the foam tape into 3 pieces (2x approximately 0.5 cm length for the sides of the recess in the bottom plate, 1x approximately 3 cm length for the clamp) and glue them into place.

<table>
  <tr>
    <td></td>
    <td></td>
  </tr>
</table>

- Insert the Raspberry Pi in the bottom of the case (the sd-card must not be installed jet).
- Close the case by snapping in the lid to the bottom.
- Insert the sd-card to the card slot.
- Put the complete Raspberry Pi, mounted in the case, in the recess at the bottom plate.
- secure it with the clamp and screw it into place with a metal screw (2.9 x 9.5 mm) with an applied washer.

<table>
  <tr>
    <td></td>
    <td></td>
  </tr>
</table>

### Manufacturing the USB-C Plug
- To safe some space it is recommeneded to manufacture a usb plug from slim spare parts. We use the repair kit of recable shown below.

<figure> 
   connect acdc PCB
</figure>

- First you have to cut a small triangle in on site top of the shrinking tube.

<figure> 
   connect acdc PCB
</figure>

- Remove about 2 mm of the insulation from the dc/dc converter output wires.
- Soldering the wires to the plug as shown in the picture.
- If you use the recable plug the bigger pin (on the left) is the V+ contact and the biggest pin (on the right) is the V- contact. In this case the yellow wire is the lead.

<figure> 
   connect acdc PCB
</figure>

- Now you can slide the frame of the plug over the plug until it is snap into its place.
- Bend the wire holder downwards at a right angle and guide the wires into its holder.
- Fix the wires with a pliers.

<table>
  <tr>
    <td></td>
    <td></td>
  </tr>
</table>

- Move the schrink tube over the plug. The cutted edge has to be at the bottom and at the front.
- Try to hold it in position with on hand during shrinking the tube with a heat gun. Also the right angle should be bent back in final position during heating.\
**Attention: Be carfull because of the hot air during this process to avoid burnings.**
  
<table>
  <tr>
    <td></td>
    <td></td>
  </tr>
</table>

### Installing the DC/DC Converter
- Install the DC/DC converter with the holder and screw it into place (use a screw 2.9 x 9.5 mm)

<figure> 
   connect dcdc PCB
</figure>

### Prepare power cable for router
- If you are not reusing the power cable from the RUT955 you need to make your own cable.
- You need a molex plug with two crimp contacts (2824-20) two electric wire ferrules and about 25 cm of 2 core wire
<figure> 
   
</figure>

- Take the cable and strip down the insulation by ~6 mm at the one site and ~3mm at the other side.
- Crimp down electric wire ferrules on each of the end with 6mm.

<figure> 
   
</figure>

- Crimp the molex 2824-connectors on the other end.
- Insert molex connectors into the top part of 4x4 molex plug (the pin position is also descriped on the top of the router).

<table>
  <tr>
    <td></td>
    <td></td>
    <td></td>
  </tr>
</table>

----

## Connecting componets of the deck box bottom
- In the following steps all components from before will be connected to each other
- The wiring diagram is the following

<figure> 
   
</figure>

### Connecting the Router Antennas
- Screw the antennas onto the router

<figure> 
   
</figure>

- Screw the router onto the bottom plate (using 4 screws 2.9 x 9.5 mm)

<table>
  <tr>
    <td></td>
    <td></td>
  </tr>
</table>

- Insert the Ethernet and power (12V) cables

<figure> 
   
</figure>

### Connecting power wires to PCB board
- Shorten the DC cable from the AC/DC converter to 20 cm and strip the insulation.
- Screw the cable into place on the input side (DC1 IN) of the PCB.
- Repeat the procedure for the wire of the DC-input of the weipu socket and screw it into the other input (DC2 IN) on the PCB

<figure> 
   connect acdc PCB
</figure>

- Attach two electric wire ferrules to the input wires of the dc/dc converter.
- Screw it to the output of the PCB (DC2 OUT).
- Screw the power cable of the router on the other output (DC1 OUT).
- Insert the USB-C plug into the Raspberry Pi

<figure> 
   connect acdc PCB
</figure>

### Result deckbox bottom
- Up until now the deckbox lower part should look something like this.

<figure> 
   
</figure>

----

## Finishing deckbox and attaching the deckbox cage
- You need the mounting plate/cage and the four M4 screws (incl nut and washer)

<figure> 
   
</figure>

- Screw the stainless steel cage onto the deckbox bottom (M4)

<table>
  <tr>
    <td></td>
    <td></td>
  </tr>
</table>

- Clean the seal of the deckbox
- Place the lid on top and screw it into place

<figure> 
   
</figure>

- Attach the connector caps

<figure> 
   
</figure>

- (optional) Apply stickers

---
## Manufacture power cable
Depending on the power source available on the chosen vessel, you can manufacture the corresponding power cable. 

### Power cable for 230 V AC
**Safety caution: When dealing with 230 V make sure that you do not endanger yourself and that your product is safe for usage by other people. Make sure that you have the necessary training and follow the local laws.**

- Cut 15 m cable (or length suitable for your application)
- Attach Schuko plug including cap on one side
- Attach Weipu 3 pin plug on the other side (use pin 1 and 2)

### Power cable for 9-30 V DC
- Cut 15 m cable (or length suitable for your application)
- Use brown wire as plus. Use blue wire as minus
- Attach Weipu 2 pin plug including cap to one side. Use pin 1 as minus, pin 2 as plus
- Attach plug of your choice to second end of cable

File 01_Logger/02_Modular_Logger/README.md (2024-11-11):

# Assembly Instructions

## 1. Battery and Wi-Fi Antenna

1. Place the battery into the battery holder.
2. Attach the Wi-Fi antenna.

<table>
  <tr>
    <td></td>
    <td></td>
    <td></td>
    <td></td>
  </tr>
</table>

## 2. Measurement Sensors

Attach the measurement sensors.



## 3. Mainboard and Interface Board

1. Connect the mainboard to the interface board.
2. Ensure the correct polarity of the connector.

<table>
  <tr>
    <td></td>
    <td></td>
    <td></td>
  </tr>
</table>

## 4. Screw Components and Connect Plugs

1. Screw the parts together.
2. Plug in both NTC connectors.
3. Plug in the LED and reed switch connectors.
4. Connect the charging plug.


<table>
  <tr>
    <td></td>
    <td></td>
    <td></td>
  </tr>
</table>

## 5. LED and Reed Switch

1. Attach the LED and reed switch.
2. Secure them with hot glue.



## 6. Configure SD Card

Configure the SD card with the file `loggerConfig/logger_XX_config_2024XXXXXXXX.json`. Pay attention to the following points:

1. **Filename**: 
   - Replace "XX" in the filename with the correct logger number and date in the format year/month/day/hour/minute.
   - Example: For logger 13, the filename would be `logger_13_config_202409131028.json`

2. **Logger ID**:
   - In the configuration file, the "logger_id" field must contain the correct logger number.
   - Example: `"logger_id": "13"`

3. **Wi-Fi Setup**:
   - Configure the Wi-Fi settings.
   - The first Wi-Fi login should be for the corresponding deck box.
   - You can configure up to 5 different Wi-Fi networks.

Example for Wi-Fi configuration:

```json
"wifi": [
  {
    "ssid": "Deckbox_SSID",
    "password": "Deckbox_Password"
  },
  {
    "ssid": "Second_WiFi",
    "password": "Second_Password"
  }
]
```

## 7. Connect Battery and Start Device

1. Connect the battery voltage to the mainboard.
2. Press the Boot-BMS button.
3. The board starts and can be assembled.
4. Leak test still needs to be carried out

<table>
  <tr>
    <td></td>
    <td></td>
    <td></td>
  </tr>
</table>

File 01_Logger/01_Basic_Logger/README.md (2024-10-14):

# Basic Logger

The documentation in this folder will explain how to build a basic logger for CTD and O2 with four specific sensors in hardware and software.

<figure> 
   finished_logger

   <figurecaption><a name="figure1">*Figure 1:*</a> *Basic logger without pressure housing*</figurecaption>
</figure>

1. [**Electronics**](./01_Electronics/): The electronics are used to integrate the sensors and transmit data wireless. The corresponding readme of *01_Electronics* explains which components are necessary to assemble for the desired usage.

2. [**Mechanics**](./02_Mechanics/): The readme of the corresponding subfolder *02_Mechanics* gives a detailed description, how the mechanical hardware (especially the pressure housing and mountings) is designed and how it can be manufactured and assembled.

3. [**Software**](./03_Software/): The software is mostly commented in the code. A brief description however is given in the readme of the subfolder *03_Software* including instructions on how to flash the micro controller.
 
4. [**Sensors**](./04_Sensors/): The sensors that have been tested so far are listed and described briefly in *04_Sensors*. For every sensor there is an explanation of how to connect it to the PCB and which libraries are relevant in the software.

	A cap with four sensors for CTD and Oxygen mounted is displayed in the images below.
<figure>
   cap_side
   cap_side
   
   <figurecaption><a name="figure3">*Figure 3:*</a> *Sensors mounted to the cap*</figurecaption>
 </figure>

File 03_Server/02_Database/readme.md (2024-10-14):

# HyFiVe Server - Relation Database

All information on sensors, loggers, deckunits, ships and measured data are stored in the MariaDB.

## Entity-Relational-Diagram

The structure of a relational database is defined by it's Entity-Relationship-Model. The ER model of our database is depicted below and exported incl. some dummy data in [dump-hyfivedb-202408051002.sql](./dump-hyfivedb-202408051002.sql).

During development of the ER model, we aimed to store:
- all measurement data, incl. raw and processed values
	- Examples: An analog sensor gives a voltage, which can be calculated with a formula and calibration coefficient to turbidity in NTU. In this case we would save the raw (voltage) and calculated value. It is possible to link several calculated values to one raw value, for example if you get better calibration coefficients later. 
- sufficient meta data, to comprehend a measurement even after long time
	- Examples: What was used? Which sensors, Which calibration coefficients, Which deckbox, which vessel, ...
- data, needed to operate a fleet of systems
	- Examples: Contact information of fishermen deploying our system, owner of a specific sensor, date of last calibration, ...

The above aspirations led to the complexity of the ER model. 

<figure> 
   database_ER

   <figurecaption><a name="figure1">*Figure 1:*</a> *Entity-Relational model of the HyFiVe data base*</figurecaption>
</figure>

## Installation

Installation of the mariadb-server
```
	sudo apt install mariadb-server
	sudo mysql_secure_installation
```
Create administrative user
```
	sudo mariadb
	mariaDB [(none)]> GRANT ALL ON *.* TO 'admin'@'localhost' IDENTIFIED BY 'password' WITH GRANT OPTION;
	mariaDB [(none)]> FLUSH PRIVILEGES;
	mariaDB [(none)]> exit
```
Load the dump file dump-hyfivedb-202408051002.sql. The file contains the structure of the database and two deployments. It also shows how sensors, loggers, ships and other meta information can be inserted.
```
	sudo mariadb
	mariadb --user admin_restore --password < dump.sql
```

## Backups

To have regular backups of the data a ```mariaDB_backup``` folder in the home directory of the user is created with the subfolders ```backup``` and ```backup_long```. The ```mariaDB_backup``` has a create_backup.sh file 
with a mariadb-dump statement. It copies the database and its content to a file with the current date formatted in yyyy-mm-dd_backup.sql to the folder ```backup```. The find command after delets all files older than 30 days. 
The last section saves the backup into ```backup_long``` on every first of a month. These will not be deleted

```
#!/bin/bash

message=/home/hyfiveuser/mariaDB_backup/backup/$(date +%Y-%m-%d)_backup.sql
#echo "$message"
mariadb-dump --databases hyFiveDB --user="admin" --password="tfZwSRanFaAZ" > "$message"

find /home/hyfiveuser/mariaDB_backup/backup/ -name "*.sql" -type f -mtime +30 -delete

dayOfMonth=`date '+%d'`
if [ $dayOfMonth == 01 ]
then
message=/home/hyfiveuser/mariaDB_backup/backup_long/$(date +%Y-%m-%d)_backup.sql
mariadb-dump --databases hyFiveDB --user="admin" --password="tfZwSRanFaAZ" > "$message"
fi

```

This bash file is called by the crojob once per day by
```
0 1 * * * /home/user/mariaDB_backup/create_backup.sh
``` 

For physical redundancy it is not recomended to only have a backup on one server. Therefore, this procedure should be run on a second server including the --host option refering to the server with the database.

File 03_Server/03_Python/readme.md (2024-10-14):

# HyFiVe Server - Data handling and Quality Checks with Python Scripts

To ensure the scalability of the system, we aimed for automated quality control of the measured data. This is already done by several institutions and many checks are possible for hydrographic data, e.g.: 
- Impossible position: Is the measurement position in a sea area or on land?
- Impossible depth: Is the depth above sea level or lower than the sea floor?
- False timestamp, e.g. 01.01.1970 (unix 0)?

We implemented a python script, which:
- reads in new files in mailbox/in/netcdf
- does some quality checks (until 09.2024 we only implemented a few)
- logs the results
- writes the measuring data into the database
- moves file to backup or error folder

## Measured data

Measured data arrives on the server in .nc files. For processing it there is a ```netcdf_handling``` folder in the main directory of the user structured as:
```
netcdf_handling/
	backup_files/
	files_with_problems/
	logs/
		yyyy-mm-dd.txt
	python_scripts/
		checks_list.py 
		classes_writeToDB.py
		functions_writeToDB.py
		main_writeToDB.py
		processing_rules.pkl
		
```

All of the above mentioned scripts are located in the subfolder Python/ of this readme. Incoming data is processed by ```main_writeToDB.py``` which is called by the cronjob every 15 minutes
```*/15 * * * * python3 /home/hyfiveuser/netcdf_handling/python_scripts/main_writeToDB.py > /dev/null 2>&1```

main_writeToDB.py uses functions_writeToDB.py, classes_writeToDB.py (for locations; points/polygons), checks_list.py for check specifications, processing_rules.pkl for parameter specific validity criteria.

An overview of the routine run by the script is given below.

<figure> 
   <img src="../media/flowchart_overview_routine.png"  title="Flowchart">

   <figurecaption><a name="figure1">*Figure 1:*</a> *Flowchart*</figurecaption>
</figure>

Notes for processed/raw values by the Python script:
1. **ADC value or any value that must be processed with calibration coefficients:** The value is stored in RawValue and the corresponding calibration coefficients form table CalibrationCoefficient in combination with
the calculation_rule in SensorType are used to calculate the processed value for table ProcessedValue in the next step. This makes it possible to trace the processed value back to the sensors reading (used for the 
TSYS01 by BlueRobotics). The calculation rule must be given in the form of ```f0 * c0 * val ** p0 + ... + fn * cn * val ** pn``` with fx being factors, cx being calibration coefficients and px being the power. The 
preparation of the calculation is done in the function ```get_sensor_caluclation(sensor_id, engine, time_end_deployment)```. For a smooth way of this function to run insert the fx and px to the SensorType as follows:
'[f0, f1, ..., fn], [p0, p1, ..., pn]'
2. **Pre-processed value**: Some sensors do not give a raw value with calibration coefficients and a calculation rule to handle the raw value. In this case the reading of the value from the sensor is as raw as it gets.
Therefore the value is stored in RawValue and Processed value without any math inbetween. Of course there is always the option of calibration the sensor in a lab and think of an own calculation rule to process the
read out value as raw value.

To distinguish the two above mentioned cases, the script checks for the existence of a dataframe column named "parameter_raw", e.g. "temperature_raw" in addition to the "temperature" column. If the "parameter_raw" column exists, it contains the ADC value from case 1. Else the values in "parameter" will be used and case 2 applies.

- checks if time input is an iso-string (happened a couple of times in the first nc files), then uses parser to convert this string to a datetime.datetime object. This will be obsolete in the future hopefully.
- checks if dataframe is empty.

- checks for out of range values (from the point of possible database entries, -1e12 < x <= 1e13) and sets those values to -9999.
- executes data validity checks (criteria from processing_rules.pkl), to be able to write the "valid" column of the ProcessedValue table later as whole dataframe (more time efficient than updating every single ProcessedValue entry made one by one) 
- formats entries for deployment table and writes deployment table; 
- writes raw value data; deletes deployment entries, if error occurs while writing rawvalue table for the first sensor;
- prepares and writes processed values in ProcessedValues table
- executes validity checks again, prepares and writes corresponding executed checks in CheckAtProcessedValue table
- prepares and writes ProcessedValueHasRawValue table for connection of processed and raw values.

- if successfully written in db, copies nc file to backup folder and deletes old one.
- if problems occurred while writing, the nc file gets copied to files_with_problems folder and the old file is deleted.

if some unexpected error occured, the console error message is written in the log file.

## checks_list.py and adding a check

checks_list.py contains all validity checks in the main function execute_check(). So far this is a check for outliers and a check for realistic dates (data before 1970 does not pass the test). The validity criteria come from processing_rules.pkl, a pickled file that is created and modified by processing_rules.py. More checks can be implemented by adding another elif loop in checks_list.py/execute_check() with a check_id. This check_id has also to be added in the database in the hyfiveDB.Check table. To execute the check, the check_id has to be added to the check_ids in the processing_rules.pkl, in the dictionary ['general']['check_ids'], where the main script gets the ids from.

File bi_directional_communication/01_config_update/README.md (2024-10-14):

# Updating a Logger's Configuration Remotely

## Configuration parameters and JSON file

All config parameters are stored in a config.json file, an example is given in [./logger_10_config_202405071357.json](./logger_10_config_202405071357.json). The table down below contains all config parameters with a brief description.

The modular logger uses all config parameters. The basic logger needs a correct config file, but processes only few parameters from it, as indicated in the table.

This table is also given as [excel table](./logger_config_parameters.xlsx) containing additional information (data type of parameter on modular logger and information if and how the parameter can be found in the data base). 

## Transmitting a Config File from Deck Box to Logger via MQTT

The transmission between deck box and logger is described in below flow chart:

<figure> 
   config_update_flow_diagram

   <figurecaption><a name="figure1">*Figure 1:*</a> *Transmission of config file between logger and deck box*</figurecaption>
</figure>

## Table of all Config Parameters

| Parameter name (in json syntax)                | example value             | Long name                              | Explanation                                                                                                        | Basic logger          |
| ---------------------------------------------- | ------------------------- | -------------------------------------- | ------------------------------------------------------------------------------------------------------------------ | --------------------- |
| {                                              |                           |                                        |                                                                                                                    |                       |
|     "logger_id"                                |  5,                       | Logger ID                              | Unique ID of this logger                                                                                           | used                  |
|     "operation_mode"                           | "profiling_Travemuende",  | Operation mode                         | (only needed as meta data)                                                                                         | no                    |
|     "fw_version"                               | "base",                   | Firmware version                       |                                                                                                                    | no                    |
|     "num_sensors"                              | 2                         | Number of sensors (attached to logger) | Generated automatically                                                                                            | no                    |
|     "wifi"                                     |  [                        |                                        |                                                                                                                    |                       |
|         {                                      |                           |                                        |                                                                                                                    |                       |
|             "ssid"                             |  "SSID1",                 | Wifi SSID                              |                                                                                                                    | used                  |
|             "passw"                            | "\*\*\*"                  | Wifi password                          |                                                                                                                    | used                  |
|         },                                     |                           |                                        |                                                                                                                    |                       |
|         {                                      |                           |                                        |                                                                                                                    |                       |
|             "ssid"                             |  "SSID2",                 |                                        | modular logger allows several sets of wifi credentials, which                                                      | no second set of wifi |
|             "passw"                            | "\*\*\*"                  |                                        | are checked in the given order                                                                                     |                       |
|         }                                      |                           |                                        |                                                                                                                    |                       |
|     ],                                         |                           |                                        |                                                                                                                    |                       |
|     "config_update_periode"                    | 3600,                     | Config update periode                  | interval [s] when to check for update                                                                              | hard coded            |
|     "status_upload_periode"                    | 3600,                     | Status upload periode                  | interval [s] when to upload new status                                                                             | hard coded            |
|     "sample_periode"                           | 2                         | Sample periode                         | interval [s] in which to sample (if underwater)                                                                    | hard coded            |
|     "sample_cast_enable"                       |  0,                       | Sample cast enable                     | if enabled, logger measures with different periode if down or upcast is detected                                   | no                    |
|     "sample_cast_periode"                      |  1,                       | Sample cast periode                    | interval [s] in which to sample, if logger has detected a cast                                                     | no                    |
|     "cast_det_sensor"                          |  23,                      | Cast detection sensor                  | ID of sensor for detecting a cast (usually pressure)                                                               | no                    |
|     "cast_det_sensor_threshold"                | 50,                       | Cast detection sensor threshold        | a cast is detected, if this threshold is exceeded by 'difference in sensor reading during 1s', so usually [mbar/s] | no                    |
|     "wet_det_sensor"                           |  23,                      | Wet detection sensor                   | ID of sensor for detecting the beginning of a dive                                                                 | hard coded            |
|     "wet_det_periode"                          |  15,                      | wet detection periode                  | interval [s] when to check if immersed                                                                             | used                  |
|     "wet_det_threshold"                        |  1050,                    | wet detection threshold                | if reading of wet_det_sensor > this threshold, an immersion is detected                                            | used                  |
|     "dry_det_sensor"                           | 23,                       | dry detection sensor                   | ID of sensor for detecting the end of a dive                                                                       | no                    |
|     "dry_det_threshold"                        | 1050,                     | dry detection threshold                | if reading of dry_det_sensor < this threshold, an emersion is detected                                             | no                    |
|     "dry_det_verify_delay"                     | 5,                        | dry detection verify delay             | time [s] at the end of a dive to continue measureing and check for reimmersion                                     | no                    |
|     "data_upload_retry_periode"                | 300,                      | data upload retry periode              | time [s] to wait until retry, if a data trasmission failed                                                         | hard coded            |
|     "deckunit_id"                              |  6,                       | Deckunit ID                            | (only needed as meta data), ID of primary deck box for this logger                                                 | used                  |
|     "platform_id"                              |  7,                       | Platform ID                            | (only needed as meta data), ID of platform this logger is deployed on                                              | used                  |
|     "vessel_id"                                |  7,                       | Vessel ID                              | (only needed as meta data)                                                                                         | used                  |
|     "vessel_name"                              |  "Paula",                 | Vessel name                            | (only needed as meta data)                                                                                         | used                  |
|     "deployment_contact_id"                    |  1,                       | Deployment contact ID                  | (only needed as meta data)                                                                                         | used                  |
|     "contact_first_name"                       | "Peter",                  | Contact first name                     | (only needed as meta data)                                                                                         | used                  |
|     "contact_last_name"                        | Petersen",                | Contact last name                      | (only needed as meta data)                                                                                         | used                  |
|     "sensors"                                  |  [                        |                                        | Information on all connected sensors:                                                                              |                       |
|         {                                      |                           |                                        | Information on one specific sensor:                                                                                |                       |
|             "sensor_id"                        |  11,                      | Sensor ID                              |                                                                                                                    | used                  |
|             "sample_periode_multiplier"        |  1,                       | Sample periode multiplier              | measuring period of this sensor = sample_periode \* sample_periode_multiplier                                      | no                    |
|             "sample_cast_periode_multiplier"   |  1,                       | Sample cast periode multiplier         | measuring period of this sensor during cast = sample_periode \* sample_cast_periode_multiplier                     | no                    |
|             "bus_address"                      |  2,                       | Bus address                            | Address of the interfaceboard of this sensor in the I2C bus                                                        | no                    |
|             "calib_coeff"                      |  {                        | Calibration coefficients               |                                                                                                                    | used                  |
|                 "0"                            |  \-1.128306E+1,           |                                        | 0 to 10 calib coefficients can be given to one sensor                                                              | used                  |
|                 "1"                            |  233434534                |                                        |                                                                                                                    | used                  |
|             },                                 |                           |                                        |                                                                                                                    |                       |
|             "sensor_type"                      |  {                        |                                        | All information on the type of this sensor:                                                                        |                       |
|                 "sensor_type_id"               |  7,                       | Sensor type ID                         | (only needed as meta data)                                                                                         | used                  |
|                 "parameter"                    |  "temperature",           | Parameter                              | (only needed as meta data)                                                                                         | used                  |
|                 "long_name"                    |  "sea_water_temperature", | Long name                              | (only needed as meta data)                                                                                         | used                  |
|                 "unit"                         |  "degC",                  | Unit                                   | (only needed as meta data)                                                                                         | used                  |
|                 "manufacturer"                 |  "AML",                   | Manufacturer                           | (only needed as meta data)                                                                                         | used                  |
|                 "model"                        |  "XchangeCT",             | Model                                  | (only needed as meta data)                                                                                         | used                  |
|                 "serial_number"                |  "123456",                | Serial number                          | (only needed as meta data)                                                                                         | used                  |
|                 "parameter_no"                 |  1,                       | Parameter no                           | Shall be used if a sensor can measure more than one parameter (to set the order of the parameters)                 | no                    |
|                 "accuracy"                     |  0.01,                    | Accurancy                              | (only needed as meta data)                                                                                         | used                  |
|                 "resolution"                   |  0.001                    | Resolution                             | (only needed as meta data)                                                                                         | used                  |
|             }                                  |                           |                                        |                                                                                                                    |                       |
|         },                                     |                           |                                        |                                                                                                                    |                       |
|         {                                      |                           |                                        |                                                                                                                    |                       |
|             "sensor_id"                        |  23,                      |                                        |                                                                                                                    |                       |
|             "sample_periode_multiplier"        |  2,                       |                                        |                                                                                                                    |                       |
|             "sample_periode_multiplier_upcast" |  1,                       |                                        |                                                                                                                    |                       |

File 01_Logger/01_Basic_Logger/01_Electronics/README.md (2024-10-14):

# Basic Logger - Electronics

The hardware is designed and can be modified in KiCad 7. Therefore the folder **/HyfiveLib** contains custom footprints and schematics for the projects below.

## Main PCB
The main PCB is designed to run the operations of the logger. It features an ESP32 as a micro controller and some peripheral components to integrate a wide range of sensors. To assemble a PCB for a logger follow the instructions of the [BOM.md](./BOM.md). The basic logger can implement sensors by

	- 3x I2C
	- 2x UART
	- 1x RS485

To select possible sensors to implement take a look into the subfolder [*../04_Sensors*](../04_Sensors/). The list can of course be extended. So far all sensors except the ones by BlueRobotics are connected with Molex PicoBlade connectors. How to connect each sensor in hardware is described in the sensor readme.

How to program the electronics after manufacturing is explained in the subfolder [*../03_Software*](../03_Software/).

A basic version of the PCB is shown in the image below.

<figure> 
   

   <figurecaption><a name="figure1">*Figure 1:*</a> *Main PCB inside the basic logger*</figurecaption>
</figure>

## Keller connector
  
One additional PCB, that is needed to implement a Keller 9LD pressure sensor, is given in **/KellerConnector**. The PCB can be soldered to the pins of the sensor and can then be directly connected to I2C1 (53261-0471) of the main PCB with a 4 pin Molex connector (15134-0402).

<figure> 
	

   <figurecaption><a name="figure2">*Figure 2:*</a> *Small PCB for interfacing the Keller pressure sensor*</figurecaption>
</figure>

## Battery

The power supply of the logger can be any battery pack that fits the case. We have user 12 LiPo (3,7 V, type 18650) cells in parallel (12P1S) with the connector Molex: 15136-0203. This fits to the power socket of the PCB (55935-0230).

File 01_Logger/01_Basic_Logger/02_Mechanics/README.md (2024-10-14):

# Mechanical Hardware of the HyFiVe Logger

This readme explains considerations during mechanical design and is aimed to enable the reader to reproduce or modify the hardware.

Software: The mechanical hardware was designed in the CAD software Fusion 360 from Autodesk (version 2.0.19725). All design files were exported in the .f3d file format of this software as well as the commonly used .step exchange format. 

## Pressure Housing

### General Form
The electronic components of the logger are protected by a resealable pressure housing. A cylinder with flat end caps was chosen as basic form for this housing, because it is easy to manufacture and hydrostatically favourable. The dimensions of the cylinder was chosen according to the fitted components:
- Inner diameter            = 76 mm
- Length without end caps   = 275 mm   

The room inside the cylinder is divided in three sections, which are used by the following components:
1. Sensors (approx. 100 mm length)
2. Electronics (approx. 75 mm length)
3. Batteries (approx. 65 mm length)

<figure> 
   finished_logger

   <figurecaption><a name="figure1">*Figure 1:*</a> *The room inside the logger is devided into three sections: Battery, electronics and sensors*</figurecaption>
</figure>

### Material Choice
As material of the pressure housing we compared different metal and plastic materials. We decided for plastic material, because it is lightweigt, easy to process and facilitates wireless charging as well as data transmission. As specific material we chose Polyoxymethylene (POM), since it is affordable, widely used and offers relatively good mechanical strength. 

### Calculation of Wall Thickness
The requirements for the logger contained a depth rating of 300 m. The thickness of the pressure housing was designed according to [Technical Memorandum 3-81, Woods Hole Oceanographic Institution, 1981](https://darchive.mblwhoilibrary.org/server/api/core/bitstreams/3d9f97f5-31f3-5559-85ba-1ef265a84cb4/content). The corresponding calculation is published as Excel file. 

### Sealing
For sealing the pressure housing O-rings were chosen. All connections are sealed with two O-rings, except third party products with only one inbuilt O-ring. The O-ring grooves were designed according to the [technical guide of Norelem](https://norelem.de/medias/23900-Technischer-Hinweis-O-Ringe-DE.pdf?context=bWFzdGVyfHJvb3R8MzEzNjczfGFwcGxpY2F0aW9uL3BkZnxhR1kxTDJnNE5TODVNREUxTlRJNU16Y3pOekkyTHpJek9UQXdYMVJsWTJodWFYTmphR1Z5WDBocGJuZGxhWE5mVHkxU2FXNW5aVjlFUlM1d1pHWXxkZTcyN2ZmN2VkMjcwYTA5M2RjNzFkNjc0MjMxYTQxZWMxMjZkMTQxMmRlNGU0YTVjOTY2ZThiNTI4NGNmNDE5). In favour of easy maintenance, we decided against 'pressure neutral' designs, e.g. by filling with oil or potting with resin.

The end caps are sealed with two radial O-rings of 3 mm diameter. The end caps are attached to the cylinder by three M3x16 mm screws in axial direction, to prevent accidental removal. 

## Penetrators

### Use of End Caps
The flat end caps are used to feed through sensors and other components, which need contact with the environment. The sensors are placed on one end cap, which offers space for up to six sensors. The sensors are positioned in a ring, where the centre position can't be used, as it is occupied by the electronic mounting inside. The second end cap is used for additional functionalities e.g. charging contacts, an LED and a magnetic switch. Two types of drawings are given for manufacturing: One drawing for a blank end cap and other drawings for postprocessing the specific drillings needed on both end caps. 

### Self-Designed Bushings for Sensors Without In-Built Sealings
Most of the used OEM-sensors provide an inbuilt sealing and a thread for securing. But some sensors - like the conductivity sensors from Atlas Scientific, which is designed for lab-use - do not offer an inbuilt sealing. For this type of sensors we developed a metal bushing, which is manufactured on a lathe. The bushing provides two grooves for radial O-rings, a thread to secure against accidental removal and a chamber, which is filled with Epoxy resin and seals the bushing towards the sensor shaft (this processed is described under ../04_Sensors)
<figure> 
   sensor_bushing

   <figurecaption><a name="figure2">*Figure 2:*</a> *Self designed bushing to feed lab sensors through the pressure housing*</figurecaption>
</figure>

### Pressure valve
A pressure relief valve is integrated for several reasons. The valve is opened while closing the cylinder, in this way you do not compress the air. It is also used to perform a vacuum test after assembly. You could also use it to refill the vacuum with nitrogen to avoid condensation. We used the pressure relief valve from BlueRobotics, as they offer a corresponding pump and the valve is affordable and relatively small. 

## Electronic Mountings
3D printed mountings were developed to hold the electronic components inside the logger. The mounting is attached to the same end cap the sensors are fed through. In this way all electronic components and most cables can be extracted on one side of the logger. The mounting is attached with a single screw in the centre of the cap, please see Figure 1.

Manually designing mounting, that connects more than two components in a three-dimensional room, can be a tiring and error prone job, especially if the position of the components is changing during development. To facilitate the design process, the generative design function of Fusion 360 was used. After defining surfaces, which shall be connected, and volumes, which are blocked, the software proposes different solutions. The results are organic looking, tree-like bodies, which can be easily adapted by changing the input and recalculation. 

- <figure>
   mounting_modeled
   mounting_printed
   
   <figurecaption><a name="figure3">*Figure 3:*</a> *Mounting for electronics inside logger - modeled with generative modeling in Fusion 360 (left) and 3D printed (right) (the shown mounting is for the modular logger)*</figurecaption>
 </figure>

## Self-Designed Penetrators for Charging and Integration of LED and Magnetic Sensor
These features are only available for the modular logger and descriped under [01_Logger/02_Modular_Logger/02_Mechanics/](../../02_Modular_Logger/02_Mechanics/).

<figure> 
   logger_charging

   <figurecaption><a name="figure4">*Figure 4:*</a> *Modular logger with charging contacts, LED and magnetic switch. For detailed description look there.*</figurecaption>
</figure>

## Otter board mounting
The logger can be deployed on a trawl. For this use case we developed an own mounting, which is described in the folder in [./04_otter_board_mounting](./04_otter_board_mounting/). 

<figure> 
   otter_board_mounting

   <figurecaption><a name="figure5">*Figure 5:*</a> *Self designed mounting to attach logger to an otter board of a trawl net*</figurecaption>
</figure>

## Bill of Material
The following mechanical material is needed to build a basic logger (in addition to the PCBs and electrical components).

| #  | Amount | Name                                                                  |
| -- | ------ | --------------------------------------------------------------------- |
|    |        | **Pressure cylinder**                                                     |
| 1  | 1      | Cylinder, POM, D 76/90, L 275, according to drawing                   |
| 2  | 1      | End cap for sensors, according to drawing                             |
| 3  | 1      | End cap, blank                                                        |
| 4  | 6      | Screws M3 x 14, hexagonal, stainless A4                               |
| 5  | 4      | O-ring 70 x 3, NBR70                                                  |
| 6  | 1      | O-ring lube, e.g. Molycote 44 Medium                                  |
|    |        | **Internal mounting**                                                     |
| 7  | 1      | Mounting for electronic components, 3D printed                        |
| 8  | 1      | Mounting for battery pack, 3D printed                                 |
| 9  | 3      | Tapping screw, M2.9 x 9.5, for attaching main PCB                     |
| 10 | 1      | Screws M6 x 14, hexagonal                                             |
|    |        | **Sensors and accessories**                                               |
| 11 | 1      | Temperature: BlueRobotics Celsius Fast Responde, incl. O-ring and nut |
| 12 | 1      | Pressure: Keller 20D, 50bar, incl. adapter PCB                        |
| 13 | 1      | Oxygen: Pyroscience picoO2sub incl. Oxycap-sub, O-ring and nut        |
| 14 | 1      | Conductivity: Atlas Scientific K1.0 incl. adapter board               |
| 15 | 1      | Bushing for conductivity sensor, incl. distance sleeve for potting    |
| 16 | 1      | Nut M18x1 ('Sechskant-Gegenmutter')                                   |
| 17 | 2      | O-ring, 15.5 x 2, NBR70                                               |
| 18 | 1      | Pressure valve, BlueRobotics PRV-R1, incl. O-rings and nut            |
| 19 | 1      | Vacuum pump, BlueRobotics Vacuum-Pump-R1, incl. adapter for PRV       |

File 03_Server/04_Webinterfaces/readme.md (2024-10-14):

# HyFiVe Server - Webinterfaces

We engaged a external software company to develop two interface. 

The source code for the interfaces is published in the subfolders, incl. instructions on how to install.

## Configuration Interface

Detailed information about config parameters and data transmission can be found in [bi_directional_communication](../../bi_directional_communication/).

The [configuration interface](./config_interface/) has the following functionalities: 
- Gives an overview of all loggers:
    - Currently assigned deck box and vessel
    - Status information
        - Battery remaining
        - Memory remaining
    - Last position shown on map
- Change config parameters of loggers:
    - including sensor information
    - Creating new config files
    - Also writing changes in relational data base
- Create new loggers and sensors 

The configuration interface has to interact with "two points of truth": The database and the existing config files on the server. Part of the config parameters are stored in both; some parameters are only stored in the config files. Although this complicated development, the interface reads all parameters from both sources and writes changes into both correctly. 

## Visualisation interface

The [visualisation interface](./visualisation_interface/) is reachable under [http://hyfive.info:4001](http://hyfive.info:4001) has the following functionalities:
- Visualising all measurement data in the HyFiVe database
- Giving an overview of measurements
    - Filter date, region and vessel
    - Show all corresponding measurements in a table with important meta information
    - Show all corresponding measurements on a map
- Show details of one specific measurement
    - Meta information
    - Plotting parameters over time
    - Plotting parameters over depth
    - Automated cast detection: Divides profiles (plot with parameter over depth) into three segments (downcast, upcast, rest). this is especially valuable for data measured on a trawl net.
    - Show whole track on a map
    - Intelligent zoom function, export function for plots

The visualisation interface interacts with the database by SQL requests to receive the needed measurement and meta data. 

## Pictures of Interfaces

<figure> 
   config_1_overview

   <figurecaption><a name="figure1">*Figure 1:*</a> *Config interface - Overview*</figurecaption>
</figure>

<figure> 
   config_2_logger

   <figurecaption><a name="figure2">*Figure 2:*</a> *Config interface - Logger*</figurecaption>
</figure>

<figure> 
   config_3_sensor

   <figurecaption><a name="figure3">*Figure 3:*</a> *Config interface - Sensor*</figurecaption>
</figure>

---

<figure> 
   vis_1_overview

   <figurecaption><a name="figure4">*Figure 4:*</a> *Visualisation interface - Overview*</figurecaption>
</figure>

<figure> 
   vis_2_plots1

   <figurecaption><a name="figure5">*Figure 5:*</a> *Visualisation interface - Plots Part 1*</figurecaption>
</figure>

<figure> 
   vis_2_plots2

   <figurecaption><a name="figure6">*Figure 6:*</a> *Visualisation interface - Plots Part 2*</figurecaption>
</figure>

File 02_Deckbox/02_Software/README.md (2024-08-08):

# How to Manufacture a HyFiVe Deck Box - Software

This document explains how to install and configure the software on the deck box in detail. A computer running Windows 10 has been used to set up the system with Firefox as a default browser. 

The standard username is 'admin', a standard password should be chosen and will be written as 'xxxx' in the following.

## Initial Setup of Raspberry Pi

### (Optional) Using an Image of a Working Deck Box

The fastest way to set up the Pi is to use an image of a working deck box. You can download the latest image from this Github repository (hyfive_raspberry_image` from the software folder).
Clone it to a SD card using the Raspberry Pi imager and insert in Pi. If the image is working fine, 
you only need to configure the router according to the following two chapters [Router setup](#setup-of-the-router) and [VPN setup](#setup-of-vpn-connection-to-pi).

### Initial setup

If not using an image, follow these instructions: 

1. Download and open Raspberry Pi Imager
2. Select Pi 4 and suitable 64-bit operating system (Raspberry Pi OS 64-bit)
3. Insert SD card, and chose it in Imager
4. Open Advanced settings (low right corner),  
```text
    host name               raspberrypi.local  
    Set Username            admin
    password                xxxx 
    choose local settings   ETC/UTC and de keyboard
    services                enable SSH, use password-authentification 
```
4. Write image
5. Insert SD card in Pi
6. The Pi is ready to boot.

<br/><br/>
___

## Setup of the Router

The router used is a RUT955 from Teltonika. It is set up the following way to provide a WiFi network and GPS positioning as well as work as MQTT broker and NTP server.  

### Wifi Connection and Firmware Update

Before connecting to the router, download  a new firmware for the router from Teltonika's webpage to your computer (https://wiki.teltonika-networks.com/view/RUT955_Firmware_Downloads)
This documentation is done based on version 07.06.3. If you want to use a back-up file for setting up the router, choose this version (see next chapter). 
Otherwise you can also use a newer firmware, but note that with new firmware versions the instructions might change a little. 
Especially where the settings are located in the menu. 

Power up router (SIM card not inserted), connect to its Wifi using the default passwort written on the router or by an ethernet cable.  
Open browser, enter router IP "192.168.1.1". Log into router with default user and passwort written its manual.  
Set new passwort. The login for all routers should be set to:
```text
    user: admin                       (not changed, note when logging in by ssh or CLI the user is root)
    password: xxxx!
```
If you have entered the wrong login several times, your IP gets blocked by the router. Connect via LAN cable, enter Webgui, go to system->administraion->access control->security and unblock your IP.  

Abort set-up wizard and update firmware
```text
    Go to System -> Firmware -> Upgrade via file -> chose downloaded file -> upgrade
```
Alternatively you can search for available update and upgrade via server. This takes more time, as you have to upgrade several times. After the login you need to reconnect to the wifi.  
After updating the firmware, change the mode of the webinterface from basic to advanced by clicking on basic in the top left corner of the interface.

### (Optional) Using Backup File of a Working Deck Box

Similar to using an image to set up the Pi, you can use a backup file of a working deck box to save time. 

You can download a generic backup file from this Github repository ('deckbox -> software -> deckbox_router_backup_20240422'). For this follow these steps:
1. In the router's GUI (under 192.168.1.1) navigate to `system -> Maintenance -> Backup`
2. Under `Restore Configuration`, click browse, choose the backup file, click Proceed, wait for rebooting
3. Now we individualize the deck box by giving it an unique ID. Under `Network -> Wireless -> SSIDs` click Edit. Replace the XX in the SSID with the unique ID of the manufactured deck box. 

If this setup worked you can continue with the chapter [Setup of VPN Connection to Pi](#setup-of-vpn-connection-to-pi).

### Setup wizzard

Return to the set-up wizard (system -> set-up wizard). Use default settings except:
```text
    Configuration mode: Advanced
    Time zone:      Set to UTC, update time manually
    LAN Config:     Take default values
    Mobile Config:  Auto APN, Enter pin of SIM card, chose 2G+4G
    WiFi:           Change SSID to HyfiveXX with XX equals HyFiVe Serial number of deck unit  
                    Change passwort to: xxxx!
                    Take default for other values
```
Reconnect to wifi with new password. Open webinterface again by typing IP in browser.  

To insert Sim card: Navigate to `Network->Mobile->General->SIM1` in the webinterface, doublecheck the PIN of your SIM card in PIN. 
Then power down the router, insert the SIM card in slot 1 and boot the router again. After logging in to the webinterface the router should show 
connection to the internet which is necessary for the next steps.

### NTP client

The router shall update its clock every five minutes:
```text
    System-> Administration -> Date&Time:
    Time zone                   UTC
    GPS synchronization         on
    GPS time update interval    every five minutes 
    -> NTP tab
    "enable NTP client"         on            
    Updateintervall             300 s 
```
For time synchronization enable the NTP server of the router so that the sensor carriers and Raspberry Pi can synchronize their clocks. On the same page: 
```text
    NTP Server - activate       on
```

### MQTT

The MQTT broker of the router with the IP address 192.168.1.1 is used by the sensor carriers and NodeRed on the Pi. Enable MQTT broker and external access:

First install the MQTT package (internet access required):
```text
    System -> package manager -> packages -> search 'MQTT' -> install
```
After installation:
```text 
    Services -> MQTT -> Broker:
    MQTT broker                 on
    local port                  1883
    enable remote access        on
    Broker settings -> Misc -> allow anonymous      on
```

### IP/DNS

Pi and router should be connected by LAN cable. For remote access and NMEA forwarding the IP of the Pi needs to be determined. The router will assign an IP automatically to the MAC address of the raspberry. First the MAC address of the Pi is determined by the following steps:
```text
    status->network->lan->DHCP leases->find Raspberry Pi
    if pi is not found: Status -> network -> topology -> scan lan
    Save Mac address of pi
```
Now the IP of the Pi will be permanently changed using static lease. This way the PIs in all deck boxes have the same IP.

```text
    network -> DHCP -> static lease
    Add a new instance with
        IP 192.168.1.123
        MAC address of pi
        name deckboxPi 
```

A reboot might be necessary.

### GPS
After the IP address of the Raspberry Pi is known, configure the GPS forwarding.  
Inside the router GUI:
```text
    Go to Services->GPS->General
    Enable all three NMEA supports
    Go to Services/Dienste->GPS->NMEA
        NMEA forwarding             Enable
        Hostname                    IP of Raspberry Pi (192.168.1.123)
        Protocol                    UDP
        Port                        8500
        NMEA sentence settings      GPRMC enable, forwarding interval 1 s
```
Node Red will handle the forwarded data.

<br/><br/>
___

## Setup of VPN Connection to Pi

To be able to connect to the Raspberry Pi inside the deck box even remotely over the internet, you can configure the following VPN connection. It requires a VPN server and input from the servers admin. The setup of the VPN server is documented separately. 

### Connect Own Computer to Hyfive VPN

1. Install Openvpn client
2. Receive .ovnc config file from admin (includes key, certificates)
3. Drag .ovnc file in Openvnc client and connect

### Connect Router to Hyfive VPN

1. Receive key and certification files from vpn admin.
2. Open Router Webinterface on 192.168.1.1.
3. Navigate to Services->VPN->OpenVPN
4. Enable advanced mode on top right of the GUI
5. Add new instance with name 'hyfive' as client
6. Edit VPN connection and change the following parameter:
```text
    enable          yes
    TUN/TAB         TUN (tunnel)
    Authentication  TLS
    Encryption      AES-256-GCM 256
    Remote host/IP address      hyfive.info
    Add. HMAC auth. Authentication only (tls-auth)
    Upload files for upload in following order: ta.key, ca.crt, DeckboxXX.crt and DeckboxXX.key 
```

To check, if the setup worked, you can open a ssh connection to the router via the program putty. User name is 'root' and password as set above 'xxxx'. Enter: 
```text
    ifconfig 
```   
If your IP is 10.8.0.XX you are connected via VPN. 

### Enable Port Forwarding on Router

In order to access ports on the Pi over VPN, they need to be forwarded by the router from the router's network to the VPN network. 

In the router webgui navigate to `network -> firewall -> port` forwarding. Enable advanced mode in top right of GUI. Add new instances with the following parameters. 

Take default parameter, **except** for 'Enable' ON and 'source zone', which shall be changed to OpenVPN

| Name              | External port | Internal IP address | Internal Port |
|-------------------|---------------|---------------------|---------------|
| Pi_Nodered        | 1880          | 192.168.1.123       | 1880          |
| Pi_Portainer      | 9000          | 192.168.1.123       | 9000          |
| Pi_Grafana        | 3000          | 192.168.1.123       | 3000          |
| Pi_Influx         | 8086          | 192.168.1.123       | 8086          |
| Pi_VNC            | 5900          | 192.168.1.123       | 5900          |
| Pi_SSH            | **23**        | 192.168.1.123       | **22**        |
| Pi_Webinterface   | **81**        | 192.168.1.123       | **80**        |

Note that the external port for Pi_SSH is set to 23. This way, you still access the router via SSH on port 10.8.0.XX:22 and the Pi via port 10.8.0.XX:23. In the same way you can access the webinterface of the router by entering 10.8.0.XX in the browser, while accessing the webinterface of the Pi by 10.8.0.XX:81.

### Identify Devices Connected to VPN

To check, which deck box and which user is currently connected to the VPN, and to identify their IPs, go to http://hyfive.info/ and log in with 
```text
    user:       user
    password:   yyyy
```

<br/><br/>
___

## Installation of Software on Raspberry Pi

The Raspberry Pi receives, processes, and sends data. For these tasks we use NodeRed in combination with InfluxDB. 
Both are installed inside docker containers. We choose Portainer as our docker GUI. The measuring data are visualized either using Grafana or the Hyfive Webinterface.  

Make sure you are connected to the network of the router for the following steps.

#### Find IP of Raspberry Pi

The IP of the Pi was set to 192.168.1.123 by static lease, s. above. If this did not work, the IP can be found by:
   - Option 1: &emsp; Use tool like Advanced IP Scanner  
   - Option 2: &emsp; Enter "arp -a" in cmd  
   - Option 3: &emsp; Open router webinterface in browser. Navigate `Status -> Network -> Lan/Wlan`: Here you see all connected devices

### Connect via SSH

We will use SSH connection for further configuration and installation processes. 
If not mentioned otherwise, all following commands are ment to be entered in the terminal of the Pi, accessed via SSH or VNC.

To connect to the terminal of the Pi you can use Windows command prompt (cmd) and enter: `ssh admin@192...your IP from above`.
Enter password (the password should be 'xxxx'). Don't mind, that no characters appear while typing password, just type and press enter.  

You can also use the software putty. This is recommended at least via VPN. In this case enter the IP of the Pi inside the VPN network and remember the port change/forwarding from 22 to 23, s. chapter about VPN.

### Connect via VNC

You can use VNC as a tool to transfer files to the Pi and as alternative to SSH for accessing its terminal. 

To use VNC you first need to enable it via SSH. Type into the Pis terminal:
```text
    sudo raspi-config
    Go to Interfacing Options->VNC->enable  
```
In VNC Viewer: `File -> New connection->` Enter IP of the deck box. Connect and enter user + password.

Comments on file transfer: Preferably use VNC Viewer because it comes with the best file transfer tool. Nevertheless, TigerVNC is recommended for newest PI OS Versions. TigerVNC can be installed from https://github.com/TigerVNC/tigervnc/releases. VNC Viewer is capable of transferring folders. In case you are using TigerVNC, folders needs to be ziped first. 

### Set NTP to Router

First keep your system up to date:
```text
    sudo apt-get update
    sudo apt-get upgrade -y
```

Synchronize Raspberry Pi and router time:
```text
    sudo timedatectl set-timezone UTC
    sudo timedatectl set-ntp true
    sudo nano /etc/systemd/timesyncd.conf
        add the line:
            FallbackNTP=192.168.1.1
            timedatectl status
        exit with ctrl+x, save
```

### Docker Installation

```text
    curl -fsSL https://get.docker.com -o get-docker.sh
    sudo sh get-docker.sh
```

Test Docker:
```text
    sudo docker run hello-world
```

### Portainer Installation

Install Portainer into Docker. On April 2024 the `portainer/portainer-ce` version encountered a bug during installation of Python packages. Therefore use the alternative/last line in the first half of 2024.
```text
        sudo docker volume create portainer_data
        Choose
            default (latest stable version): sudo docker run -d -p 9000:9000 -p 8000:8000 --name portainer --restart always -v /var/run/docker.sock:/var/run/docker.sock -v portainer_data:/data portainer/portainer-ce
            alternative (version 2.20.1, 2024): sudo docker run -d -p 8000:8000 -p 9000:9000 --name=portainer --restart=always -v /var/run/docker.sock:/var/run/docker.sock -v portainer_data:/data portainer/portainer-ce:2.20.1
```
Open Portainer webgui in your browser by entering 192.168.1.123:9000. Add your credentials: 
```text 
        - User:admin
        - PW: xxxx
```
Choose "get started/local" as your environment

### Node-Red Installation

Install Node Red into Docker:
```text
    sudo docker volume create nodeRedData
    sudo docker run -d -it -p 1880:1880 -p 8500:8500/udp -v nodeRedData:/data --restart always --name nodered nodered/node-red
```
To install nodes, which are not preinstalled but needed, open nodered webgui 192.168.1.123:1880 (or 10.8.0.XX:1880 via VPN) in a browser. Navigate to menu (top right) -> manage palette -> installation and install the following packages:
```text
    - node-red-contrib-json
    - node-red-contrib-influxdb
    - node-red-contrib-sftp
```
Instead you can also install packages with essential nodes via command prompt inside the nodered container by entering it trough Portainer:
```text
    sudo docker exec -it nodered /bin/bash
    npm install node-red-contrib-json
    npm install node-red-contrib-influxdb
    npm install node-red-contrib-sftp
    npm update
    exit
```
This results in 8 vulnerabilities found (5 low, 3 moderate) by npm audit, which cannot be fixed by npm audit -fix. 
Uncertain if this is a problem and if this happens also by installing the nodes manually via webgui.

To install all required python libraries for executing python scripts, open Portainer by typing 192.168.1.123:9000 (VPN: 10.8.0.XX:9000) in your browser. 
Navigate to NodeRed Container (`local -> Container -> nodered)`, click on `>_ Console`, enter root as user and connect. Then: 
```text
    apk update
    apk upgrade
    apk add py3-pip
    apk add py3-numpy
    apk add py3-pandas
    apk add py3-scipy
    apk add expect
    apk add py3-matplotlib
    apk add py3-xarray
    pip install influxdb-client
```
Click disconnect.

### Grafana Installation 

Install Grafana into Docker:
```text
    sudo docker run -d  --name=grafana1 --restart always -p 3000:3000 grafana/grafana:latest
```
First your credentials are:

        - User: admin
        - PW: admin

Change it during first login on webgui 192.168.1.123:3000 to:
    
        - User:admin
        - PW: xxxx

### InfluxDB Installation 

Install InfluxDB into Docker:
```text
    sudo docker volume create influxdbData
    sudo docker run -it -d -p 8083:8083 -p 8086:8086 --name influxDB -v influxdbData:/var/lib/influxdb --restart always influxdb
```
In browser open InfluxDB webgui 192.168.1.123:8086. Enter your credentials:
```text
    username                    admin
    password                    xxxx
    Initial organisation name   hyfive
    Initial bucket name         localhyfive
    Continue, save your token!
    Continue in advanced setup
```

<br/><br/>
___
## Configuring Software on Raspberry Pi

### Restart Policy of containers in Portainer

Normally, each restart policy is set to `restart-always` by default. Double-check the default setting:

Open Portainer GUI under port 192.168.1.123:9000.
Select container, scroll to bottom, check restart "Restart Policy", if necessary change policy to "always".

### Bridge Network in Portainer

This bridge network enables its members to reach and call each other by their container names, instead of using IPs.

In Portainer GUI (192.168.1.123:9000) navigate to `Networks -> Add network`. Use following input and save
```text
    Name                                OwnBridge
    IP4 network config Subnet           172.19.0.0/16
```
Navigate to `Containers -> nodered -> Connected networks` join the Ownbridge network. Repeat for InfluxDB and Grafana.  

### Create Buckets in InfluxDB

Inside Influx webgui 192.168.1.123:8086, navigate to buckets. Create:
```text
    Bucket with name GpsBuffer and 'delete data older than 72 h'
```

Navigate to `API tokens -> generate API token` to generate an all access token named `hyfivetoken` and save this one well.

### Connecting Grafana and Influx

Open Grafana Gui on 192.168.1.123:3000. Navigate to `Connections -> Data sources -> search and add data source 'InfluxDB'`. Add the two data sources, by doing the following twice:

```text
    Name            'InfluxDB_GpsBuffer' and 'InfluxDB_localhyfive'
    Query language  Flux
    URL             http://influxDB:8086
    Base auth       disable
    Organisation    hyfive  
    Token           Insert token (all-access token 'hyfivetoken')
    Default bucket  'GpsBuffer' and 'localhyfive'
```
Now you can configure an own Dashboard to visualize measurement data. This is not further explained, as we use our own visualisation webinterface as default. 

<br/><br/>
___
## Node-RED Setup

### Importing Flow to Nodered and connect to InfluxDB

Open Nodered GUI under 192.168.1.123:1880. Import recent HyFiVe flow from this subfolder. 
Select `menu (top right) -> import -> choose file for import` and upload deckunit_01_NodeRed.json .  

For Nodered to be able to write data into InfluxDB, you need to enter your specific token. For this modify an influxdb node, e.g. 'influxdb batch' 
node called `Save GPS` by double-clicking its icon. Edit the server 'LocalInflux' by clicking the pencil symbol. 
Since all influx nodes in the flow use the server 'LocalInflux', you only need to enter the token at one node. Enter:
```text
    Token		all access hyfivetoken from above
    Save and exit node
    Deploy changes (top right corner)
```

### NetCDF 

To export data in NetCDF format, two python files needs to be loaded into the nodered container.
Final NetCDF files will be saved in a netcdf folder.

Open the nodered terminal inside the Pi's terminal:
```text
    sudo docker exec -it nodered /bin/bash
```
Enter:
```text
    mkdir netcdf
    mkdir python_scripts
    nano python_scripts/loadLocalData.py
        Copy text from GitHub MultiParamterLogger/AP3_Deckunit/03_Software/netcdf/loadLocalData.py (paste with right mouse click)
        exit with control+x and save
    nano python_scripts/create_netcdf.py
        Open Python script MultiParamterLogger/AP3_Deckunit/03_Software/netcdf/createOnPi.py in text editor, replace the token in line 18 with your all access hyfivetoken.
        Copy text from createOnPi.py with your new token
        exit and save
    nano python_scripts/recent_deployments.json
        Add the following text:
            {} 
        exit and save
    exit
```

Now, nodered is able to create NetCDF files via an execute node.

Note, that executing the scripts with an empty data base, will result in an error shown in the debug window of Nodered. This error will not compromise other functions of the deck box.

### Configuring SFTP in NodeRed

SFTP is needed to transfer the netCDF files to the server onshore and pick up configuration files. We enable nodered to trigger SFTP by editing it's container:

```text
    sudo docker exec -it nodered /bin/bash
    mkdir handle_data
    nano handle_data/push_sftp.sh
        copy the following text in the editor : 
            #!/usr/bin/expect
            spawn sftp loggermailbox@hyfive.info
            expect "password:"
            send "xxyy\n"
            expect "sftp>"
            send "put -r /usr/src/node-red/netcdf /in\n"
            expect "sftp>"
            send "exit\n"
            interact
        exit with control+x, save
    chmod 777 handle_data/push_sftp.sh
    nano handle_data/get_configs.sh
	copy the following text in the editor:
		#!/usr/bin/expect
		spawn sftp loggermailbox@hyfive.info
		expect "password:"
		send "xxyy\n"
		expect "sftp>"
		send "get -r /out/config/ /usr/src/node-red/\n"
		expect "sftp>"
		send "exit\n"
		interact
	exit with control+x, save
    chmod 777 handle_data/get_configs.sh
```

First connection to sftp server needs to be done manually (while still being in the nodered terminal):
```text
    sftp loggermailbox@hyfive.info
        continue 
        type in passwort: xxyy 
```
You can also paste the by right mouse click. Per default no characters of the password typed will be shown, just type and press enter. 

Confirm the connection. Close sftp by entering 'exit' as well as the terminal of Nodered by another 'exit'.

___
## Grafana Setup
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

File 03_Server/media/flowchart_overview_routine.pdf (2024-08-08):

get list of filenames in mailbox/in/netcdf

read in nc-file data

false

perform tests to check hardware setup 1.) check_logger_sensor_config() 2.) ---

-check_for_duplicate_nc_files() | true
-check if filename is already in DB

get next filename from all filenames list

pick column (parameter) with values, that has sensor_id, except for pressure

use column_raw as raw
values and calculate
processed values with
get_sensor_calculation()

use column as raw
values and processed
values
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

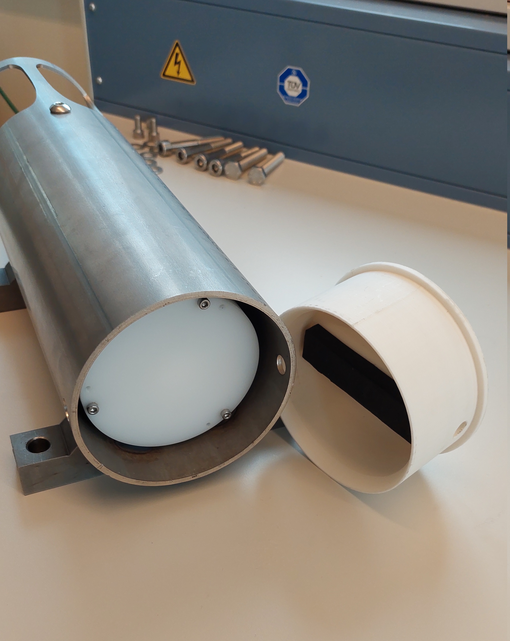
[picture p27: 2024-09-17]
01_Logger/01_Basic_Logger/02_Mechanics/04_otter_board_mounting/media/Insert_logger.jpg

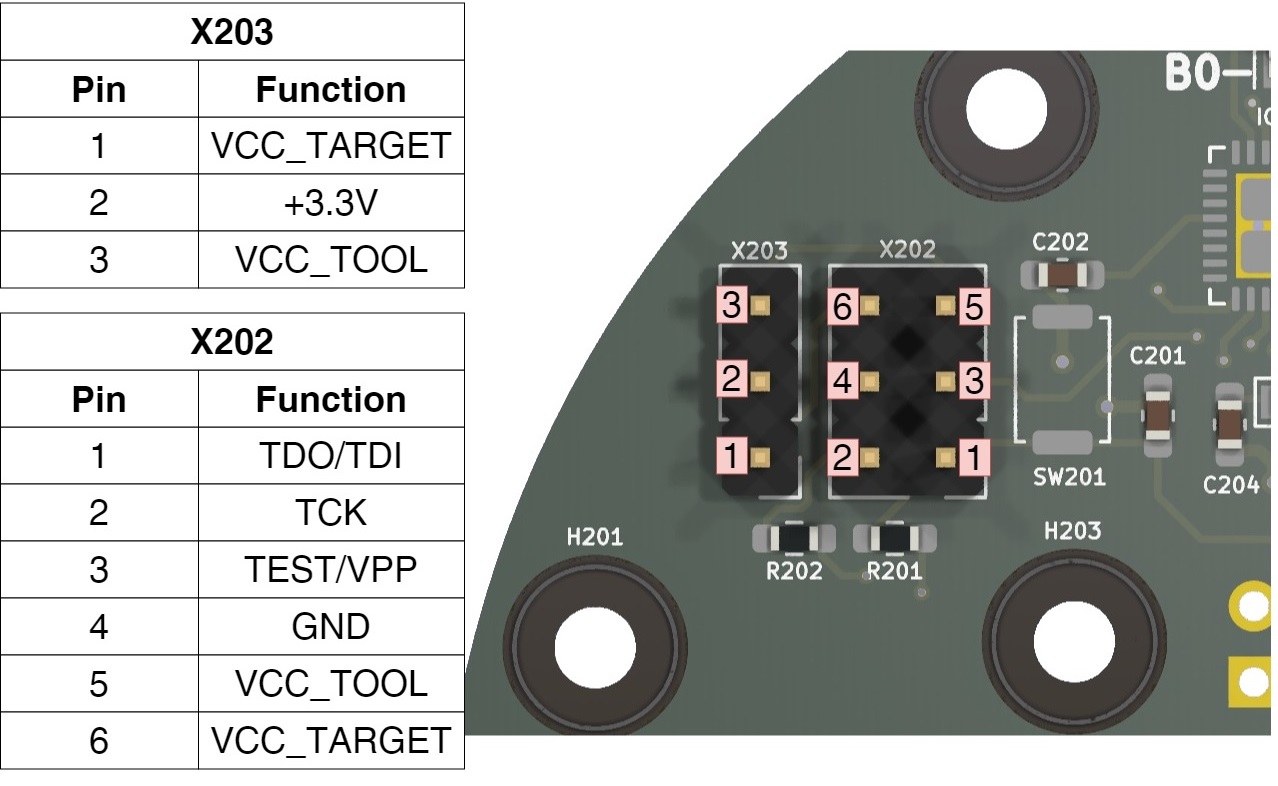
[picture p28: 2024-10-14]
01_Logger/02_Modular_Logger/01_Electronics/media/JTAG_Connector.jpg

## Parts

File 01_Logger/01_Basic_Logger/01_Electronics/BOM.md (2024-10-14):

# Basic Logger - Electronics - Bill of Material

# Main PCB
  
To manufacture the electronic hardware of a logger order the PCB in **/Rev_01** at the manufacturer of your choice. To assemble the PCB to your needs follow the instructions and the bill of materials in the tables below. The schematics and board design in **/Rev_01** provide additional information for the assembly.  

 **Note:** The connection between the hardware and software is very close in this embedded design. Understanding and testing the the hardware in detail is highly recommended before usage. GPIOs of the micro controller are used in the code to switch components such as sensors and the SD card and can lead to errors in case of changes.

## Main Components for PCB Rev_01

These are components needed in any case to run the micro controller and his basic functions.

U3 is used to protect the power supply from deep discharge. With the combination of R22 and R21 it will turn everything off, when the battery falls below 3.55 V. If this is not needed, bridge pin 7 & 8 of U3.

**Note:** when using Blue Robotics sensors, I2C1 and I2C2 should be replaced with BM04B-GHS-TBT to connect them easily.
|Reference|Amount|Value|Footprint|Manufacturer Part Number|
| :---: | :---: | :---: | :---: | :---: |
|C1|1|10n|Capacitor_SMD:C_0805_2012Metric||
|C7, C8|2|1µ|Capacitor_SMD:C_0805_2012Metric||
|H1, H2, H3|3|MountingHole|MountingHole:MountingHole_3.2mm_M3||
|H4, H5|2|MountingHole|MountingHole:MountingHole_3.2mm_M3_DIN965||
|I2C1, I2C2|2|Conn_01x04_MountingPin|Connector_Molex:Molex_PicoBlade_53261-0471_1x04-1MP_P1.25mm_Horizontal|53261-0471|
|I2C3_5Pin1|1|Conn_01x05_MountingPin|Connector_Molex:Molex_PicoBlade_53261-0571_1x05-1MP_P1.25mm_Horizontal|53261-0571|
|J9|1|Micro_SD_Card|Hyfive:GCT_MEM2067-02-180-00-A_REVB|MEM2067-02-180-00-A|
|Molex_Battery1|1|Conn_01x02|Connector_Molex:Molex_MicroClasp_55935-0230_1x02_P2.00mm_Horizontal|55935-0230|
|Molex_Usb1|1|Conn_01x06_MountingPin|Connector_Molex:Molex_PicoBlade_53261-0671_1x06-1MP_P1.25mm_Horizontal|53261-0671|
|Q1, Q2, Q5|3|SS8050-G|Package_TO_SOT_SMD:SOT-23-3|SS8050-G|
|Q6|1|BSS83P|Package_TO_SOT_SMD:SOT-23|MMFTP84|
|R7, R8, R13, R14|4|10k|Resistor_SMD:R_0603_1608Metric||
|R15, R16|2|1k|Resistor_SMD:R_0603_1608Metric||
|R18, R19|2|15k|Resistor_SMD:R_0603_1608Metric||
|R20|1|2M2|Resistor_SMD:R_0603_1608Metric||
|R21, R25, R26|3|1M|Resistor_SMD:R_0603_1608Metric||
|RTC1|1|Conn_01x08|Hyfive:DS3231Module|3013|
|SW1|1|SW_DIP_x01|Button_Switch_SMD:SW_DIP_SPSTx01_Slide_6.7x4.1mm_W8.61mm_P2.54mm_LowProfile|434111025826|
|U2|1|RT9080-33GJ5|Package_TO_SOT_SMD:SOT-23-5|RT9080-33GJ5|
|U3|1|LTC1540|Package_SO:SOIC-8-1EP_3.9x4.9mm_P1.27mm_EP2.29x3mm|LTC1540CS8#TRPBF|
|U4|1|ESP32-S3-WROOM-1|PCM_Espressif:ESP32-S3-WROOM-1U|ESP32-S3-WROOM-1U-N16R2|

## Optional components according to the used sensors

### UART1 with boost converter (13V) and optional RS485

These components enable a higher supply voltage for one sensor. The voltage can be adjusted by the setup of R3, R23, R2 and R24.
|Reference|Amount|Value|Footprint|Manufacturer Part Number|
| :---: | :---: | :---: | :---: | :---: |
|C18|1|10µ|Capacitor_SMD:C_0805_2012Metric|TMK212BBJ106KG8T|
|C19|1|10n|Capacitor_SMD:C_0805_2012Metric||
|C20|1|2,2n|Capacitor_SMD:C_0805_2012Metric||
|C21|1|4,7µ|Capacitor_SMD:C_0805_2012Metric|GCM21BC71E475KE36L|
|D2|1|D_Schottky|Diode_SMD:D_1206_3216Metric|CD1206-B240|
|IC1|1|MP3213DH-LF-Z|Package_SO:MSOP-8-1EP_3x3mm_P0.65mm_EP1.95x2.15mm|MP3213DH-LF-Z|
|L2|1|4,7µ|Inductor_SMD:L_Bourns-SRN4018|SRN4018-4R7M|
|Q3|1|SS8050-G|Package_TO_SOT_SMD:SOT-23-3|SS8050-G|
|Q4|1|BSS83P|Package_TO_SOT_SMD:SOT-23|MMFTP84|
|R2, R24|2|12k|Resistor_SMD:R_0603_1608Metric||
|R3, R23|2|470k|Resistor_SMD:R_0603_1608Metric||
|R4, R5, R22|3|15k|Resistor_SMD:R_0603_1608Metric||
|R9, R10|2|100k|Resistor_SMD:R_0603_1608Metric||
|Uart2_RS485_V8|1|Conn_01x04_MountingPin|Connector_Molex:Molex_PicoBlade_53261-0471_1x04-1MP_P1.25mm_Horizontal|53261-0471|

### UART1 or RS485

For using UART1 use
|Reference|Amount|Value|Footprint|Manufacturer Part Number|
| :---: | :---: | :---: | :---: | :---: |
|R40, R42|2|0|Resistor_SMD:R_0603_1608Metric||

For using RS485 use
|Reference|Amount|Value|Footprint|Manufacturer Part Number|
| :---: | :---: | :---: | :---: | :---: |
|R6, R12|2|1k|Resistor_SMD:R_0603_1608Metric||
|R41, R43|2|0|Resistor_SMD:R_0603_1608Metric||
|U1|1|THVD14x9|Package_SO:SOIC-8_3.9x4.9mm_P1.27mm|THVD1429DT|

### UART2, 3.3V

UART2 runs with 3.3V and can be switched off by a high side switch.
|Reference|Amount|Value|Footprint|Manufacturer Part Number|
| :---: | :---: | :---: | :---: | :---: |
|Q9|1|SS8050-G|Package_TO_SOT_SMD:SOT-23-3|SS8050-G|
|Q10|1|BSS83P|Package_TO_SOT_SMD:SOT-23|MMFTP84|
|R1, R11|2|100k|Resistor_SMD:R_0603_1608Metric||
|R29, R30|2|15k|Resistor_SMD:R_0603_1608Metric||
|Uart2|1|Conn_01x04_MountingPin|Connector_Molex:Molex_PicoBlade_53261-0471_1x04-1MP_P1.25mm_Horizontal|53261-0471|

# External components to implement the sensors and power the system

|Reference|Amount|Function|Manufacturer Part Number|
| :---: | :---: | :---: | :---: |
|Molex connector I2C|4|Connect 4 pin I2C sensor|Molex: 15134-0402|
|Molex connector I2C|1|Connect 5 pin I2C sensor|Molex: 15134-0502|
|Molex connector UART|1|Connect programmer|Molex: 15134-0602|
|Molex connector V+|1|Connect power|Molex: 15136-0203|
|Molex Antenna|1|Improve connection of ESP|Molex: 47950-0011|
|UART Progammer|1|Programm the ESP32 with code|Digilent: 410-212|

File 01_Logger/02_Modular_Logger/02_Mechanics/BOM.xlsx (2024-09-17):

# | Amount | Name
 |  | Pressure cylinder
1 | 1 | Cylinder, POM, D 76/90, L 275, according to drawing
2 | 1 | End cap for sensors, according to drawing
3 | 1 | End cap for charing, according to drawing
4 | 6 | Screws M3 x 14, hexagonal, stainless A4
5 | 4 | O-ring 70 x 3, NBR70
6 | 1 | O-ring lube, e.g. Molycote 44 Medium
 |  | Internal mounting
7 | 1 | Mounting for electronic components, 3D printed
8 | 1 | Mounting for battery pack, 3D printed
9 | 4 | Tapping screw, M2.9 x 9.5, for attaching main PCB
10 | 1 | Screws M6 x 14, hexagonal
11 | 2 | Thread rod M2.5, length 75 mm
12 | 4 | Nuts M2.5
 |  | Sensors and accessories
13 | 1 | Temperature: BlueRobotics Celsius Fast Responde, incl. O-ring and nut
14 | 1 | Pressure: Keller 20D, 50bar, incl. adapter PCB
15 | 1 | Oxygen: Pyroscience picoO2sub incl. Oxycap-sub, O-ring and nut
16 | 1 | Conductivity: Atlas Scientific K1.0 incl. adapter board
17 | 1 | Bushing for conductivity sensor, incl. distance sleeve for potting
18 | 1 | Nut M18x1 ('Sechskant-Gegenmutter')
19 | 2 | O-ring, 15.5 x 2, NBR70
20 | 1 | Pressure valve, BlueRobotics PRV-R1, incl. O-rings and nut
21 | 1 | Vacuum pump, BlueRobotics Vacuum-Pump-R1, incl. adapter for PRV
 |  | Penetrators Charging side
22 | 2 | Penetrator for charging, according to drawing
23 | 4 | O-ring 8.5x 1.5, NBR70
24 | 2 | Nut M10, hexagonal, flat, stainless A4, DIN439/ISO4035
25 | 2 | Washer with single head solder terminal, M2.2xM10.2, tinned copper
26 | 1 | Mounting for reed switch incl. 1 M3x8 hex screws

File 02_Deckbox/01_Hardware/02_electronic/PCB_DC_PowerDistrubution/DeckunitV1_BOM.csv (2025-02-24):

Part | Value | Device | Package | Description | DIGIKEY_PARTNO | MANUFACTURER | MPN | PACKAGE
D1 | CDBA360-HF | SS12 | SMA | DIODE SCHOTTKY 60V 3A DO214AC | CDBA360-HF | Comchip Technology | SS12 | SMA (DO-214AC)
D2 | CDBA360-HF | SS12 | SMA | DIODE SCHOTTKY 60V 3A DO214AC | CDBA360-HF | Comchip Technology | SS12 | SMA (DO-214AC)
F1 | ESKA PTF/18SMD 5A 230V | 65800001109 | 65800001109 | FUSE BLOK CARTRIDGE 250V 10A SMD | WK6249TR-ND | Littelfuse Inc. | 65800001109 | 65800001109
X1 | DC1 IN | 22-23-20212PIN | 2PIN | Schraubklemmblock 1.5mm2 2-Pin RM3.5 | 277-1721-ND | Phoenix Contacts | 1984617 | 2 PIN Through-Hole
X2 | DC2 IN | 22-23-20212PIN | 2PIN | Schraubklemmblock 1.5mm2 2-Pin RM3.5 | 277-1721-ND | Phoenix Contacts | 1984617 | 2 PIN Through-Hole
X3 | DC1 OUT | 22-23-20212PIN | 2PIN | Schraubklemmblock 1.5mm2 2-Pin RM3.5 | 277-1721-ND | Phoenix Contacts | 1984617 | 2 PIN Through-Hole
X4 | DC2 OUT | 22-23-20212PIN | 2PIN | Schraubklemmblock 1.5mm2 2-Pin RM3.5 | 277-1721-ND | Phoenix Contacts | 1984617 | 2 PIN Through-Hole

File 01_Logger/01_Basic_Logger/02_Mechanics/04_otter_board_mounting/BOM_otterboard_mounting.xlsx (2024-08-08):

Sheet: BOM
# | Amount | Name | Comment
1 | 1 | Mouting - Pipe, watercut, according to drawing
2 | 2 | Mounting - Feet, watercut, according to drawing
3 | 1 | Stencil for welding, water cut, according to drawing
4 | 1 | Stencil for drilling, water cut, according to drawing
5 | 1 | Inlay front, 3D printed
6 | 1 | Inlay back, 3D printed
7 | 2 | Rubber mat, 3D printed (TPU)
8 | 1 | Bolt, stainless A4, according to drawing
9 | 2 | Securing pin for bolt, 3.2x20 mm, stainless A4
10 | 4 | Screw, M10x50, stainless A4 | connection to otter board
11 | 4 | Screw, M10x70, stainless A4 | connection to otter board
12 | 3 | Screw, M8x8, stainless A4, hex, pan head (ISO 7380-1) | Holing front inlay
13 | 4 | Washer M10, stainless A4
14 | 4 | Washer M10 small, stainless A4
15 | 6 | Nut M10, stainless A4, selfsecuring
16 | 1 | Selfgluing foam 80x15x10 mm
Worksteps needed
1 | 1 | Order watercutting of pipe and feet
2 | 4 | Drill Hole 10 mm in Mounting Foot
3 | 2 | Weld mounting foot to mounting pipe
4 | 1 | Manufacture securing bolt
5 | 2 | 3D print inlay
6 | 3 | Cut M8 thread in front inlay
7 | 1 | Drill holes in drill jig fitting to specific feet
8 | 2 | 3 D print rubber mat for feet of mounting
10 | 1 | Glue foam to back inlay

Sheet: Shopping List
# | Amount | Unit | Name | Done | Comment
6 | 10 | pc | Securing pin for bolt, 3x20 mm, V4A
7 | 3 | pc | Screw, M8x130, V4A |  | Backup for Bolt
8 | 10 | pc | Screw, M10x50, V4A
9 | 10 | pc | Screw, M10x70, V4A
10 | 8 | pc | Screw, M8x8, V4A, flat head |  | Holing front inlay
11 | 10 | pc | Washer small, M10, V4A | Workshop?
12 | 10 | pc | Washer wide, M10, V4A | Workshop?
13 | 0 | pc | Nut, M10, V4A | Workshop?
14 | 0 | pc | Nut, M10, V4A, selfsecuring | Workshop?
15 | 0 | pc | Nut, M8, V4A | Workshop?
16 | 0 | pc | Nut, M8, V4A, selfsecuring | Workshop?

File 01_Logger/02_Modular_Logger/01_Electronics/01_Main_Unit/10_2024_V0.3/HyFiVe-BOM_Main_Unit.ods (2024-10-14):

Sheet: Main Unit
Qty | Value | Seriennummer | Device | Package | Parts | Bestücken? | Description | Kommentar | Verfügbar | Hersteller
1 | 1µF 10V |  | Keramikkondensator | C0603 | C504 | Ja
1 | 47µF 35V X7R | KCM55WR7YA476MH01K | Keramikkondensator | C2220 | C501 | Ja |  |  | Ja | Murata
23 | 100nF 50V |  | Keramikkondensator | C0603 | C502, C503, C505, C506, C507, C511, C513, C514, C515, C801, C802, C806, C807, C809, C812, C813, C815, C816, C817, C818, | Ja
1 | 33nF 25V |  | Keramikkondensator | C0603 | C508, | Ja
2 | 47µF 35V | EDK476M025A9GAA | Elko | SMD, D = 6,3mm H = 5,4mm | C509, C517, | Ja |  |  | Ja | Kemet
2 | 1µF 35V |  | Keramikkondensator | C0603 | C510, C512, | Ja
2 | 20µF 35V | EDK226M035A9DAA | Elko | SMD, D = 5mm H = 5,3mm | C516, C518, | Ja |  |  | Ja | Kemet
1 | 22pF 35V |  | Keramikkondensator | C0603 | C519, | Ja
1 | 10µF, 50V | 860020672010 | Elko | THT Radial D = 5.0mm, H = 11.0mm, P =2.00mm | C601, | Ja |  |  | Ja | Würth
2 | 22µF 30V |  | Keramikkondensator | C0805 | C602, C603 | Ja
1 | 150pF, 2kV | CC1206JKNPODBN151 | Keramikkondensator | C1206 | C604 | Ja |  |  | Ja | Yageo
2 | 47µF 10V |  | Keramikkondensator | C0805 | C605, C606 | Ja
1 | 10nF, 50V |  | Keramikkondensator | C0603 | C803 | Ja
4 | 100pF 50V |  | Keramikkondensator | C0603 | C804, C805, C810, C814, | Ja
1 | 2,2µF 100V |  | Keramikkondensator | C1812 | C808 | Ja
1 | 100pF 100V |  | Keramikkondensator | C0603 | C811, | Ja
1 |  | BAT54W | Diode | Diode SOD-523 | D501, | Ja
2 |  | SS1H10-E3/61T | Diode | Diode SMA | D801, D803, | Ja
1 |  | MMSZ5246B-7-F | Zenerdiode | Diode SOD-123 | D802, | Ja |  |  | Ja | Diodes Incorpated
1 |  | SF-1206S1200R-2 | Fuse 12A |  | F801 | Ja | normale Fuse |  | Ja | Littlefuse
1 |  | BQ24618 | Charger | VQFN-24-1 EP4x4mm P0.5mm EP2.45x2.45mm | IC501 | Ja | Drawing RGE | Kann beigestellt werden, wenn nicht verfügbar! | Nein | Texas Instruments
1 |  | BQ40Z80 | BMS | VQFN-32-1 EP4x4mm P0.4mm EP1.4x1.4mm ThermalVias | IC801 | Ja | Drawing RSM | Kann beigestellt werden, wenn nicht verfügbar! | 6 | Texas Instruments
1 |  | SFMC-107-01-L-D | 2x7 PinSocket | 02x07_1.27mm | J101 | Ja
4 |  | 53047-0210 | Molex Connector Pico Blade |  | J502, J801 | Ja
1 |  | 43650-0215 | Molex Connector Microfit 3.0mm |  | J501 | ja
1 |  | 43650-0515 | Molex Connector Microfit 3.0mm |  | J802 | ja
3 |  | SI7101DN-T1-GE3 | MOSFET PMOS | PowerPAK 1212-8 Single | K501, K502, K505 | Ja | Vds = 30V, Id=35A, Vgsth=1,2V |  | Ja | Vishay
2 |  | SiS412DN | MOSFET NMOS | PowerPAK 1212-8 Single | K503, K504 | Ja | Vds = 30V, Id=12A, Vgsth=1V |  | Ja | Vishay
1 |  | 2N7002KW | MOSFET NMOS | SOT-323 / SC-70 | K801 | Ja |  |  | Ja | onsemi
2 |  | CSD18540Q5B | MOSFET NMOS | TDSON-8-1 | K802, K804 | Ja |  |  | Ja | Texas Instruments
1 |  | DMP6023LSS-13 | MOSFET PMOS | SOIC-8 3.9x4.9mm P1.27mm | K803 | Ja | Vds = 60V, Id=6A, Vgsth=2V |  | Ja | Diodes Incorpated
1 | 3,3µH | SRP1245C-3R3M | Festinduktivität | SRP1245C-3R3M | L501 | Ja |  |  | Ja | Bourns
1 | 10µH | CC453232A-100KL | Festinduktivität | CC453232A-100KL | L601 | Ja |  |  | Ja | Bourns
1 | 0 |  | Widerstand | R0603 | R513, | Ja
13 | 10k |  | Widerstand | R0603 | R502, R507, R701, R702, R802, R809, | Ja
1 | 51 |  | Widerstand | R0603 | R806 | Ja
1 | 100 |  | Widerstand | R0603 | R501 | Ja
1 | 5k7 |  | Widerstand | R0603 | R503 | Ja
2 | 2k7 |  | Widerstand | R0603 | R601, R605, | Ja
5 | 100k |  | Widerstand | R0603 | R506, R509, R510, R520, | Ja
1 | 232k |  | Widerstand | R0603 | R508 | Ja
2 | 680k |  | Widerstand | R0603 | R603, R607, | Ja
1 | 9k13 |  | Widerstand | R0603 | R504 | Ja | Wert richtet sich nach eingesetztem NTC
1 | 430k |  | Widerstand | R0603 | R505 | Ja | Wert richtet sich nach eingesetztem NTC
4 | 100 |  | Widerstand | R0603 | R511, R812, R814, R815, | Ja
5 | 1k |  | Widerstand | R0603 | R512, R519, R604, R608, R808, | Ja
4 | 49,9k 0,1% |  | Widerstand | R0603 | R514, R515, R516, R523, | Ja
3 | 47k |  | Widerstand | R0603 | R602, R606, | Ja
2 | 10m 2W | PCS2512DR0100ET | Widerstand | R2512 | R517, R521, | Ja |  |  | Ja | Ohmite
1 | 10 |  | Widerstand | R0603 | R518, | Ja
1 | 357k 0,1% |  | Widerstand | R0603 | R522 | Ja
1 | 1,1k |  | Widerstand | R0603 | R801 | Ja
3 | 10M |  | Widerstand | R0603 | R803, R807, R810, | Ja
1 | 4,81k |  | Widerstand | R0603 | R804 | Ja
1 | 510 |  | Widerstand | R0603 | R805 | Ja
1 | 46.4 5W | z.B. : 356047RJT | Widerstand | R4527 | R811 | Ja |  |  | Ja | TE Connectivity
1 | 1m |  | Widerstand | R1206 | R813, | Ja
4 | 499 |  | Widerstand | R0603 | R816, R817, R818, R819, | Ja
2 |  | SKRK | Taktile Pushbutton | 3,9x2,9mm | SW801 | Ja |  |  | Ja | Alps Alpine
2 |  | BSS123 | Nmos Mosfet | SOT-23 | Q601, Q603, | Ja | 0.17A Id, 100V Vds, N-Channel MOSFET, SOT-23
2 |  | IRLML5203TRPBF | Pmos Mosfet | SOT-23 | Q602, Q604, | Ja | -4.3A Id, -12V Vds, 50mOhm Rds, P-Channel HEXFET Power MOSFET, SOT-23
1 |  | TSR 1-2433E | DC-DC-Converter | 3Pin THT | U602 | Ja | 6-36V Input, Vout = 3,3V, Iout = 1A |  | Ja | Traco
1 |  | TSR 1-2450 | DC-DC-Converter | 3Pin THT | U603 | Ja | 7-36V Input, Vout = 5,0V, Iout = 1A |  | Ja | Traco
1 |  | SPBW06F-12 | DC-DC-Converter | 7 Pin THT | U601 | Ja | 9-36V Input, Vout = 12,0V, Iout = 500mA |  | Ja | Meanwell

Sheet: main_MCU
Qty | Value | Seriennummer | Device | Package | Parts | Bestücken? | Description | Kommentar | Verfügbar | Hersteller
2 | 20pF |  | Keramikkondensator | C0603 | C301, C302, | Ja
23 | 100nF 50V |  | Keramikkondensator | C0603 | C303, C304, C305, | Ja
1 |  | FTS-107-01-F-D | 2x7 PinHeader | 02x07_1.27mm | J102 | Ja
4 |  | 53047-0210 | Molex Connector Pico Blade |  | J301, J303, | Ja
1 |  |  | Pinheader | PinHeader 2x02 P2.54mm Vertikal | J304 | Ja
1 |  |  | Pinheader | PinHeader 2x04 P2.54mm Horizontal | J302 | nein
1 |  | 693071020811 | Micro SD-Card Slot |  | J701 | Ja |  |  | Ja | Würth
14 | 10k |  | Widerstand | R0603 | R302, R303, R304, R305, R308, R309, R310, R701, R702, | Ja
1 | 75 |  | Widerstand | R0603 | R307 | Ja
5 | 100k |  | Widerstand | R0603 | R301, | Ja
3 | 47k |  | Widerstand | R0603 | R306, | Ja
1 | 1M |  | Widerstand | R0603 | R703 | Ja
2 |  | SKRK | Taktile Pushbutton | 3,9x2,9mm | SW301, | Ja |  |  | Ja | Alps Alpine
1 |  | BSS138 | Nmos Mosfet | SOT-23 | Q301, | Ja | 50V Vds, 0.22A Id, N-Channel MOSFET, SOT-23
1 |  | MAX16125WTEG00+T | Reset Controller | WLP6 | U301 | Ja
1 |  | DS3231MZ | RTC | SOIC-8 3.9x4.9mm P1.27mm | U303 | Ja
1 |  | ESP32-S3-WROOM-1U-N16R8 | MCU | ESP32-S3-WROOM-1U | U302 | Ja |  |  | Ja | Espressif

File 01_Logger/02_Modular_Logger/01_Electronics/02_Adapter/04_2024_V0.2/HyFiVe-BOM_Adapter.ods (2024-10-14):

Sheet: RS232-Adapter
Qty | Value | Seriennummer | Device | Package | Parts | Bestücken? | Description | Kommentar | Verfügbar | Hersteller
1 | 1nF |  | Keramikkondensator | C0603 | C201 | Ja
2 | 1µF, <200m ESR |  | Keramikkondensator | C0603 | C202, C206 | Ja
2 | 20pF |  | Keramikkondensator | C0603 | C203,C204 | Ja
1 | 4,7µF |  | Keramikkondensator | C0603 | C207 | Ja
8 | 100nF 10-20V |  | Keramikkondensator | C0603 | C301,C205,C307,C302,C303,C305,C306,C304 | Ja
2 |  | SMBJ8.0CA | TVS-Diode, Bidirektional | SMB (DO-214-AA) | D301,D302 | Ja |  |  | Ja | Bourns, versch.
1 |  | MSP430FR2673 | MCU | VQFN-32-1EP, 5x5mm, Pitch 0.5mm, EP3.5x3.5mm | IC201 | Ja |  |  | Ja | Texas Instruments
1 |  | MAX3221E | RS-232 Transceiver | SSOP-16, 5.3x6.2mm, Pitch 0.65mm | IC301 | Ja | Mit ESD-Protection |  | Ja | Texas Instruments oder Maxim
1 |  | BSH105,215 | NMOS-FET | SOT-23 | K301 | Ja
1 | 47k |  | Widerstand | R0603 | R201 | Ja
1 | 330 |  | Widerstand | R0603 | R202 | Ja
1 |  | SKRKAEE020 | Drucktaster | 5x3mm, Pad 2.1x0.8mm, Pad-Pitch 4.2mm | SW201 | Ja |  |  | Ja | Alps Alpine
1 |  | A6H-8101 | DIP-Switch | DIP-Switch SMD 16 Pin | SW202 | Ja |  | Alternativ: 218-8LPSTJF | Ja | Omron
1 |  | ESQ-104-13-G-D | Stapelbarer Pinheader/Buchse | PinSocket_2x04_P2.54mm Vertical | X201 | Ja | Pinlänge: 12.19mm, Sockelhöhe: 13.59mm |  | Ja | Samtec
1 |  |  | Pinheader 2x3 | PinHeader_2x03_P2.54mm Vertical | X202 | Ja
1 |  |  | Pinheader 1x3 | PinHeader_1x03_P2.54mm Vertical | X203 | Ja
1 |  | 105314-1114 | Molex Nano-Fit Steckverbinder | 2x07 Pitch 2.50mm_Horizontal | X301 | Ja | 2x07, 90° Steckerbuchse, THT Mit Verriegelung, Pitch 2,5mm | Alternativ: 105314-1214 105314-1314 105314-1414 | Ja | Molex
1 |  | 9HT11-32.768KDZF-T | 32,768kHz Crystal | SMD 2x 2.0x1.2mm, Pad-Pitch 1.4mm | Y201 | Ja |  |  | Ja | TXC
2 | 10k |  | Widerstand | R0603 | R204,R203 | Nein
1 |  | 1053081214 | Molex Nano-Fit Steckverbinder | 2x07 Pitch 2.50mm_Horizontal |  |  | Stecker passend zur Buchse X301 |  |  | Molex
 |  | 105325-1007 | Molex Nano-Fit Terminal Position Assurance (TPA) |  |  |  | Zusätzliche Sicherung der Kontakte am Stecker |  | Ja | Molex
 |  | 79758-2130 | Molex Nano-Fit PreCrimped Cable |  |  |  | 30 AWG Kabel 300mm

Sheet: RS485-Adapter
 |  |  |  |  |  |  |  |  | 29.06.22
Qty | Value | Seriennummer | Device | Package | Parts | Bestücken? | Description | Kommentar | Verfügbar | Hersteller
1 | 1nF |  | Keramikkondensator | C0603 | C201 | Ja
2 | 1µF, <200m ESR |  | Keramikkondensator | C0603 | C202, C206 | Ja
2 | 20pF |  | Keramikkondensator | C0603 | C203,C204 | Ja
1 | 4,7µF |  | Keramikkondensator | C0603 | C207 | Ja
2 | 100nF |  | Keramikkondensator | C0603 | C301,C205 | Ja
1 |  | 824022 | TVS-Diode, 2x Bidirektional | SOT-23 | D301 | Ja | Alternativ SM712 (z.B.: SM712.TCT) |  | alt.
1 |  | MSP430FR2673 | MCU | VQFN-32-1EP, 5x5mm, Pitch 0.5mm, EP3.5x3.5mm | IC201 | Ja |  |  | Ja
1 |  | ADM3061 | RS485 Transceiver | SOIC-8, 3.9x4.9mm, Pitch 1.27mm | IC301 | Ja |  |  | NEIN
1 |  | BSH105,215 | NMOS-FET | SOT-23 | K301 | Ja
1 | 47k |  |  | R0603 | R201 | Ja
1 | 330 |  |  | R0603 | R202 | Ja
1 | 120 |  |  | R0603 | R301 | Ja
1 |  | SKRKAEE020 | Drucktaster | 5x3mm, Pad 2.1x0.8mm, Pad-Pitch 4.2mm | SW201 | Ja |  |  | Ja | Alps Alpine
1 |  | A6H-8101 | DIP-Switch | DIP-Switch SMD 16 Pin | SW202 | Ja |  | Alternativ: 218-8LPSTJF | Ja | Omron
1 |  | ESQ-104-13-G-D | Stapelbarer Pinheader/Buchse | PinSocket_2x04_P2.54mm Vertical | X201 | Ja | Pinlänge: 12.19mm, Sockelhöhe: 13.59mm |  | Ja | Samtec
1 |  |  | Pinheader 2x3 | PinHeader_2x03_P2.54mm Vertical | X202 | Ja
1 |  |  | Pinheader 1x3 | PinHeader_1x03_P2.54mm Vertical | X203 | Ja
1 |  | 105314-1114 | Molex Nano-Fit Steckverbinder | 2x07 Pitch 2.50mm_Horizontal | X301 | Ja | 2x07, 90° Steckerbuchse, THT Mit Verriegelung, Pitch 2,5mm | Alternativ: 105314-1214 105314-1314 105314-1414 | Ja | Molex
1 |  | 9HT11-32.768KDZF-T | 32,768kHz Crystal | SMD 2x 2.0x1.2mm, Pad-Pitch 1.4mm | Y201 | Ja |  |  | Ja | TXC
2 | 10k NB |  |  | R0603 | R204,R203 | Nein
1 |  | 1053081214 | Molex Nano-Fit Steckverbinder | 2x07 Pitch 2.50mm_Horizontal |  |  | Stecker passend zur Buchse X301 |  |  | Molex

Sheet: UART-Adapter
 |  |  |  |  |  |  |  |  | 29.06.22
Qty | Value | Seriennummer | Device | Package | Parts | Bestücken? | Description | Kommentar | Verfügbar | Hersteller
1 | 1nF |  | Keramikkondensator | C0603 | C201 | Ja
2 | 1µF, <200m ESR |  | Keramikkondensator | C0603 | C202, C206 | Ja
2 | 20pF |  | Keramikkondensator | C0603 | C203, C204 | Ja
1 | 4,7µF |  | Keramikkondensator | C0603 | C207 | Ja
2 | 100nF |  | Keramikkondensator | C0603 | C301, C205 | Ja
1 |  | RCLAMP0582B | TVS-Diode, 2x Bidirektional | SC-75 | D301 | Ja |  |  | Ja | Semtech
1 |  | MSP430FR2673 | MCU | VQFN-32-1EP, 5x5mm, Pitch 0.5mm, EP3.5x3.5mm | IC201 | Ja |  |  | Ja | Texas Instruments
1 |  | TXB0102DCU | Levelshifter | VSSOP-8 | IC301 | Ja |  |  | Ja | Texas Instruments
1 |  | BSH105,215 | NMOS-FET | SOT-23 | K301 | Ja
1 | 47k |  | Widerstand | R0603 | R201 | Ja
1 | 330 |  | Widerstand | R0603 | R202 | Ja
1 | 0 |  | Widerstand | R0603 | R302 | Ja | Entweder R302 ODER R303 bestücken! | Achtung Kurzschlussgefahr
1 |  | SKRKAEE020 | Drucktaster | 5x3mm, Pad 2.1x0.8mm, Pad-Pitch 4.2mm | SW201 | Ja |  |  | Ja | Alps Alpine
1 |  | A6H-8101 | DIP-Switch | DIP-Switch SMD 16 Pin | SW202 | Ja |  | Alternativ: 218-8LPSTJF | Ja | Omron
1 |  | ESQ-104-13-G-D | Stapelbarer Pinheader/Buchse | PinSocket_2x04_P2.54mm Vertical | X201 | Ja | Pinlänge: 12.19mm, Sockelhöhe: 13.59mm |  | Ja | Samtec
1 |  |  | Pinheader 2x3 | PinHeader_2x03_P2.54mm Vertical | X202 | Ja
1 |  |  | Pinheader 1x3 | PinHeader_1x03_P2.54mm Vertical | X203 | Ja
1 |  | 105314-1114 | Molex Nano-Fit Steckverbinder | 2x07 Pitch 2.50mm_Horizontal | X301 | Ja | 2x07, 90° Steckerbuchse, THT Mit Verriegelung, Pitch 2,5mm | Alternativ: 105314-1214 105314-1314 105314-1414 | Ja | Molex
1 |  | 9HT11-32.768KDZF-T | 32,768kHz Crystal | SMD 2x 2.0x1.2mm, Pad-Pitch 1.4mm | Y201 | Ja |  |  | Ja | TXC
2 | 10k |  | Widerstand | R0603 | R204, R203 | Nein
1 | 0 |  | Widerstand | R0603 | R303 | Nein | Entweder R302 ODER R303 bestücken! | Achtung Kurzschlussgefahr
1 |  | 1053081214 | Molex Nano-Fit Steckverbinder | 2x07 Pitch 2.50mm_Horizontal |  |  | Stecker passend zur Buchse X301 |  |  | Molex

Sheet: I2C-Adapter
 |  |  |  |  |  |  |  |  | 29.06.22
Qty | Value | Seriennummer | Device | Package | Parts | Bestücken? | Description | Kommentar | Verfügbar | Hersteller
1 | 1nF |  | Keramikkondensator | C0603 | C201 | Ja
2 | 1µF, <200m ESR |  | Keramikkondensator | C0603 | C202, C206 | Ja
2 | 20pF |  | Keramikkondensator | C0603 | C203, C204 | Ja
1 | 4,7µF |  | Keramikkondensator | C0603 | C207 | Ja
1 |  | RCLAMP0582B | TVS-Diode, 2x Bidirektional | SOT-416 | D301 | Ja |  |  | Ja
1 |  | MSP430FR2673 | MCU | VQFN-32-1EP, 5x5mm, Pitch 0.5mm, EP3.5x3.5mm | IC201 | Ja |  |  | Ja | Texas Instruments
1 |  | TXS0102DCU | Levelshifter | VSSOP-8 | IC301 | Ja |  |  | NEIN | Texas Instruments
1 |  | BSH105,215 | NMOS-FET | SOT-23 | K301 | Ja
1 | 47k |  | Widerstand | R0603 | R201 | Ja
1 | 330 |  | Widerstand | R0603 | R202 | Ja
1 | 0R |  | Widerstand | R0603 | R302 | Ja
1 |  | SKRKAEE020 | Drucktaster | 5x3mm, Pad 2.1x0.8mm, Pad-Pitch 4.2mm | SW201 | Ja |  |  | Ja | Alps Alpine
1 |  | A6H-8101 | DIP-Switch | DIP-Switch SMD 16 Pin | SW202 | Ja |  | Alternativ: 218-8LPSTJF | Ja | Omron
1 |  | ESQ-104-13-G-D | Stapelbarer Pinheader/Buchse | PinSocket_2x04_P2.54mm Vertical | X201 | Ja | Pinlänge: 12.19mm, Sockelhöhe: 13.59mm |  | Ja | Samtec
1 |  |  | Pinheader 2x3 | PinHeader_2x03_P2.54mm Vertical | X202 | Ja
1 |  |  | Pinheader 1x3 | PinHeader_1x03_P2.54mm Vertical | X203 | Ja
1 |  | 105314-1114 | Molex Nano-Fit Steckverbinder | 2x07 Pitch 2.50mm_Horizontal | X301 | Ja | 2x07, 90° Steckerbuchse, THT Mit Verriegelung, Pitch 2,5mm | Alternativ: 105314-1214 105314-1314 105314-1414 | Ja | Molex
1 |  | 9HT11-32.768KDZF-T | 32,768kHz Crystal | SMD 2x 2.0x1.2mm, Pad-Pitch 1.4mm | Y201 | Ja |  |  | Ja | TXC
4 | 10k |  | Widerstand | R0603 | R203, R204, R301, R304 | NEIN | R203 + R204 NB R301 & R304 nicht notwendig, da interner 10k Pullup vorhanden. Siehe Datenblatt TXS0102 S. 15.
1 | 0R |  | Widerstand | R0603 | R303 | NEIN
1 |  | 1053081214 | Molex Nano-Fit Steckverbinder | 2x07 Pitch 2.50mm_Horizontal |  | Ja | Stecker passend zur Buchse X301 |  |  | Molex

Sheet: Analog-Adapter
Qty | Value | Seriennummer | Device | Package | Parts | Bestücken? | Description | Kommentar | Verfügbar | Hersteller
1 | 1nF, 6,3V |  | Keramikkondensator | C0603 | C201 | Ja
2 | 1µF, <200m ESR |  | Keramikkondensator | C0603 | C202, C206 | Ja
2 | 20pF, 6,3V |  | Keramikkondensator | C0603 | C203, C204 | Ja
3 | 100nF, 6,3V |  | Keramikkondensator | C0603 | C205, C301, C302 | Ja
1 | 4,7µF 6,3V |  | Keramikkondensator | C0603 | C207 | Ja
1 |  | 82356050101 | TVS Diode | D0603 | D301 | Ja
1 |  | MSP430FR2673 | MCU | VQFN-32-1EP, 5x5mm, Pitch 0.5mm, EP3.5x3.5mm | IC201 | Ja
1 |  | TXB0104PW | Levelshifter | TSSOP-154 | IC301 | Ja
1 |  | BSH105,215 | NMOS-FET | SOT-23 | K301 | Ja |  | BSH105,215
1 | 47k |  | Widerstand | R0603 | R201 | Ja
1 | 330 |  | Widerstand | R0603 | R202 | Ja
2 | 10k NB |  | Widerstand | R0603 | R203, R204 | Nein
1 | 20k |  | Widerstand | R0603 | R301 | Ja
1 | 38,8k/39k 0,1% |  | Widerstand | R0603 | R302 | Ja
1 | 0 NB |  | Widerstand | R0603 | R303 | Nein
1 | 0 |  | Widerstand | R0603 | R304 | Ja
1 |  | SKRKAEE020 | Drucktaster | 5x3mm, Pad 2.1x0.8mm, Pad-Pitch 4.2mm | SW201 | Ja
1 |  | A6H-8101 | DIP-Switch | DIP-Switch SMD 16 Pin | SW202 | Ja
1 |  | ESQ-104-13-G-D | Stapelbarer Pinheader/Buchse | PinSocket_2x04_P2.54mm Vertical | X201 | Ja | Pinlänge: 7,36mm, Sockelhöhe: 11,05mm Alternativ: ESQ-104-13-L-D ESQ-104-13-T-D | Einbau: Pins auf Oberseite
1 |  |  | Pinheader 2x3 | PinHeader_2x03_P2.54mm Vertical | X202 | Ja
1 |  |  | Pinheader 1x3 | PinHeader_1x03_P2.54mm Vertical | X203 | Ja
1 |  |  | Conn_02x07_Top_Bottom | Connector_Molex:Molex_Nano-Fit_105314-xx14_2x07_P2.50mm_Horizontal | X301 | Ja
1 |  | 9HT11-32.768KDZF-T | 32,768kHz Crystal | SMD 2x 2.0x1.2mm, Pad-Pitch 1.4mm | Y201 | Ja
1 |  | 1053081214 | Molex Nano-Fit Steckverbinder | 2x07 Pitch 2.50mm_Horizontal |  | Nein | Stecker passend zur Buchse X301

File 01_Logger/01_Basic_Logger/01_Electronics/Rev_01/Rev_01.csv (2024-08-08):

Source: | C:\Users\Mathis Bjoerner\Documents\GitHub\HyFiVe\01_LoggingUnit\01_Electronics\Rev_01\Rev_01.kicad_sch
Date: | 21.03.2024 14:42:21
Tool: | Eeschema 7.0.8
Generator: | C:\Program Files\KiCad\7.0\bin\scripting\plugins/bom_csv_grouped_by_value.py
Component Count: | 69
Collated Components:
Item | Qty | Reference(s) | Value | LibPart | Footprint | Datasheet | DNP | Description | Function | Height | Manufacturer_Name | Manufacturer_Part_Number | Mouser | Mouser Part Number | Mouser Price/Stock
1 | 2 | C1, C19 | 10n | Device:C | Capacitor_SMD:C_0805_2012Metric | ~ |  |  | mandatory
2 | 2 | C7, C8 | 1µ | Device:C | Capacitor_SMD:C_0805_2012Metric | ~ |  |  | mandatory
3 | 1 | C18 | 10µ | Device:C | Capacitor_SMD:C_0805_2012Metric | ~ |  |  | vsensor |  |  | TMK212BBJ106KG8T | https://www.mouser.de/ProductDetail/Taiyo-Yuden/TMK212BBJ106KG8T?qs=sGAEpiMZZMuMW9TJLBQkXvBULEti4LCQVeEoQfarTPE%3D
4 | 1 | C20 | 2,2n | Device:C | Capacitor_SMD:C_0805_2012Metric | ~ |  |  | vsensor
5 | 1 | C21 | 4,7µ | Device:C | Capacitor_SMD:C_0805_2012Metric | ~ |  |  | vsensor |  |  | GCM21BC71E475KE36L | https://www.mouser.de/ProductDetail/Murata-Electronics/GCM21BC71E475KE36L
6 | 1 | D2 | D_Schottky | Device:D_Schottky | Diode_SMD:D_1206_3216Metric | ~ |  |  | vsensor |  |  | CD1206-B240 | https://www.mouser.de/ProductDetail/Bourns/CD1206-B240?qs=VNGG2InBe5GgEVvEEGas0A%3D%3D
7 | 3 | H1, H2, H3 | MountingHole | Mechanical:MountingHole | MountingHole:MountingHole_3.2mm_M3 | ~ |  |  | mandatory
8 | 2 | H4, H5 | MountingHole | Mechanical:MountingHole | MountingHole:MountingHole_3.2mm_M3_DIN965 | ~ |  |  | mandatory
9 | 4 | I2C1, I2C2, Uart2, Uart2_RS485_V8 | Conn_01x04_MountingPin | Connector_Generic_MountingPin:Conn_01x04_MountingPin | Connector_Molex:Molex_PicoBlade_53261-0471_1x04-1MP_P1.25mm_Horizontal | ~ |  |  | mandatory |  |  | 53261-0471 | https://www.mouser.de/ProductDetail/Molex/53261-0471?qs=%252B72YyncTwW9e3et3PwnEMw%3D%3D
10 | 1 | I2C3_5Pin1 | Conn_01x05_MountingPin | Connector_Generic_MountingPin:Conn_01x05_MountingPin | Connector_Molex:Molex_PicoBlade_53261-0571_1x05-1MP_P1.25mm_Horizontal | ~ |  |  | mandatory |  |  | 53261-0571 | https://www.mouser.de/ProductDetail/Molex/53261-0571?qs=Z4ettq%2Fvyk9tUNWvtq%2FUoA%3D%3D
11 | 1 | IC1 | MP3213DH-LF-Z | SamacSys_Parts:MP3213DH-LF-Z | Package_SO:MSOP-8-1EP_3x3mm_P0.65mm_EP1.95x2.15mm | http://www.monolithicpower.com/DesktopModules/DocumentManage/API/Document/getDocument?id=882 |  | 700KHz/1.3MHz Boost Converter With a 3.5A switch | vsensor | 1.1 | Monolithic Power Systems (MPS) | MP3213DH-LF-Z | https://www.mouser.de/ProductDetail/Monolithic-Power-Systems-MPS/MP3213DH-LF-Z | 946-MP3213DHLFZ | https://www.mouser.co.uk/ProductDetail/Monolithic-Power-Systems-MPS/MP3213DH-LF-Z?qs=rC7bBWoQAAnCxv9Q6CXi3Q%3D%3D
12 | 1 | J9 | Micro_SD_Card | Connector:Micro_SD_Card | Hyfive:GCT_MEM2067-02-180-00-A_REVB | http://katalog.we-online.de/em/datasheet/693072010801.pdf |  |  | mandatory |  |  | MEM2067-02-180-00-A | https://www.mouser.de/ProductDetail/GCT/MEM2067-02-180-00-A?qs=KUoIvG%2F9IlYTw%2Fcc1GlNJA%3D%3D
13 | 1 | L2 | 4,7µ | Device:L | Inductor_SMD:L_Bourns-SRN4018 | ~ |  |  | vsensor |  |  | SRN4018-4R7M | https://www.mouser.de/ProductDetail/Bourns/SRN4018-4R7M?qs=UvjENeDOEed%2FCjy5nMh3Xg%3D%3D
14 | 1 | Molex_Battery1 | Conn_01x02 | Connector_Generic:Conn_01x02 | Connector_Molex:Molex_MicroClasp_55935-0230_1x02_P2.00mm_Horizontal | ~ |  |  | mandatory |  |  | 55935-0230 | https://www.mouser.de/ProductDetail/Molex/55935-0230?qs=iFujUUZFeMLRagf%2FET0QzQ%3D%3D
15 | 1 | Molex_Usb1 | Conn_01x06_MountingPin | Connector_Generic_MountingPin:Conn_01x06_MountingPin | Connector_Molex:Molex_PicoBlade_53261-0671_1x06-1MP_P1.25mm_Horizontal | ~ |  |  | mandatory |  |  | 53261-0671 | https://www.mouser.de/ProductDetail/Molex/53261-0671?qs=%252B72YyncTwW9Wyr77z4J2cA%3D%3D
16 | 5 | Q1, Q2, Q3, Q5, Q9 | SS8050-G | SamacSys_Parts:SS8050-G | Package_TO_SOT_SMD:SOT-23-3 | https://datasheet.datasheetarchive.com/originals/distributors/DKDS-12/229454.pdf |  | Bipolar Transistors - BJT NPN TRANSISTOR 1.5A 40V | mandatory | 1.15 | Comchip Technology | SS8050-G | https://www.mouser.de/ProductDetail/onsemi/NSVMMBT5550LT1G?qs=W%2FMpXkg%252BdQ4rIPP%252BeFoT1g%3D%3D | 750-SS8050-G | https://www.mouser.co.uk/ProductDetail/Comchip-Technology/SS8050-G?qs=LLUE9lz1YbcHg%252BWLMAtcrQ%3D%3D
17 | 3 | Q4, Q6, Q10 | BSS83P | Transistor_FET:BSS83P | Package_TO_SOT_SMD:SOT-23 | http://www.farnell.com/datasheets/1835997.pdf |  |  | vsensor |  |  | MMFTP84 | https://www.mouser.de/ProductDetail/Infineon-Technologies/BSS83P-H6327?qs=wsCKvrPXYigax2dMaqBHWg%3D%3D
18 | 4 | R1, R9, R10, R11 | 100k | Device:R | Resistor_SMD:R_0603_1608Metric | ~ |  |  | uart2
19 | 2 | R2, R24 | 12k | Device:R | Resistor_SMD:R_0603_1608Metric | ~ |  |  | vsensor
20 | 2 | R3, R23 | 470k | Device:R | Resistor_SMD:R_0603_1608Metric | ~ |  |  | vsensor
21 | 8 | R4, R5, R17, R18, R19, R22, R29, R30 | 15k | Device:R | Resistor_SMD:R_0603_1608Metric | ~ |  |  | vsensor
22 | 4 | R6, R12, R15, R16 | 1k | Device:R | Resistor_SMD:R_0603_1608Metric | ~ |  |  | rs485
23 | 4 | R7, R8, R13, R14 | 10k | Device:R | Resistor_SMD:R_0603_1608Metric | ~ |  |  | mandatory
24 | 1 | R20 | 2M2 | Device:R | Resistor_SMD:R_0603_1608Metric | ~ |  |  | mandatory
25 | 3 | R21, R25, R26 | 1M | Device:R | Resistor_SMD:R_0603_1608Metric | ~ |  |  | mandatory
26 | 4 | R40, R41, R42, R43 | 0 | Device:R | Resistor_SMD:R_0603_1608Metric | ~ |  |  | uart1
27 | 1 | RTC1 | Conn_01x08 | Connector_Generic:Conn_01x08 | Hyfive:DS3231Module | ~ |  |  | mandatory |  |  | 3013 | https://www.mouser.de/ProductDetail/Adafruit/3013?qs=qrYS%2FWt5A16Mfm4Z0v0kNg%3D%3D
28 | 1 | SW1 | SW_DIP_x01 | Switch:SW_DIP_x01 | Button_Switch_SMD:SW_DIP_SPSTx01_Slide_6.7x4.1mm_W8.61mm_P2.54mm_LowProfile | ~ |  |  | mandatory |  |  | 434111025826 | https://www.mouser.de/ProductDetail/Wurth-Elektronik/434111025826?qs=wr8lucFkNMV8GC0fIi%2FYYw%3D%3D
29 | 1 | U1 | THVD14x9 | SymbolsModule:THVD14x9 | Package_SO:SOIC-8_3.9x4.9mm_P1.27mm |  |  |  | rs485 |  |  | THVD1429DT | https://www.mouser.de/ProductDetail/Texas-Instruments/THVD1429DT?qs=l7cgNqFNU1gMF%2Fq%2FbyikQg%3D%3D
30 | 1 | U2 | RT9080-33GJ5 | 2022-07-13_14-28-25:RT9080-33GJ5 | Package_TO_SOT_SMD:SOT-23-5 |  |  |  | mandatory |  |  | RT9080-33GJ5 | https://www.digikey.de/de/products/detail/richtek-usa-inc/RT9080-33GJ5/6161634
31 | 1 | U3 | LTC1540 | Comparator:LT1011 | Package_SO:SOIC-8-1EP_3.9x4.9mm_P1.27mm_EP2.29x3mm | https://www.analog.com/media/en/technical-documentation/data-sheets/lt1011.pdf |  |  | mandatory |  |  | LTC1540CS8#TRPBF | https://www.mouser.de/ProductDetail/Analog-Devices/LTC1540CS8TRPBF?qs=hVkxg5c3xu%2FWAnwZW1A4Hg%3D%3D
32 | 1 | U4 | ESP32-S3-WROOM-1 | PCM_Espressif:ESP32-S3-WROOM-1 | PCM_Espressif:ESP32-S3-WROOM-1U | https://www.espressif.com/sites/default/files/documentation/esp32-s3-wroom-1_wroom-1u_datasheet_en.pdf |  |  | mandatory |  |  | ESP32-S3-WROOM-1U-N16R2

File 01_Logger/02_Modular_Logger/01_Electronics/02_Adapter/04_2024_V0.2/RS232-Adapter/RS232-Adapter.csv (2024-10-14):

Source: | P:\HY501_HyFiVe\Software\MultiParamterLogger\AP2_Logger\01_Electronic\02_Adapter\RS232-Adapter\RS232-Adapter.kicad_sch
Date: | 14.09.2022 13:54:03
Tool: | Eeschema (6.0.1)
Generator: | C:\Program Files\KiCad\6.0\bin\scripting\plugins/bom_csv_grouped_by_value_with_fp.py
Component Count: | 33
Ref | Qnty | Value | Cmp name | Footprint | Description | Vendor
C201, | 1 | 1nF | C | Capacitor_SMD:C_0603_1608Metric_Pad1.08x0.95mm_HandSolder | Unpolarized capacitor
C202, | 1 | 1ÂµF, <200m ESR | C | Capacitor_SMD:C_0603_1608Metric_Pad1.08x0.95mm_HandSolder | Unpolarized capacitor
C203, C204, | 2 | 20pF | C | Capacitor_SMD:C_0603_1608Metric_Pad1.08x0.95mm_HandSolder | Unpolarized capacitor
C205, C301, C302, C303, C304, C305, C306, C307, | 8 | 100nF | C | Capacitor_SMD:C_0603_1608Metric_Pad1.08x0.95mm_HandSolder | Unpolarized capacitor
C206, | 1 | 1ÂµF | C | Capacitor_SMD:C_0603_1608Metric_Pad1.08x0.95mm_HandSolder | Unpolarized capacitor
C207, | 1 | 4,7ÂµF | C | Capacitor_SMD:C_0603_1608Metric_Pad1.08x0.95mm_HandSolder | Unpolarized capacitor
D301, D302, | 2 | SMBJ8.0CA | D_TVS | Diode_SMD:D_SMB_Handsoldering | Bidirectional transient-voltage-suppression diode
H201, H202, H203, H204, | 4 | MountingHole | MountingHole | MountingHole:MountingHole_2.7mm_M2.5 | Mounting Hole without connection
IC201, | 1 | MSP430FR2673 | MSP430FR267* | Package_DFN_QFN:VQFN-32-1EP_5x5mm_P0.5mm_EP3.5x3.5mm
IC301, | 1 | MAX3221E | MAX3221 | Package_SO:SSOP-16_5.3x6.2mm_P0.65mm | RS232 transceiver with 15kV ESD protection
R201, | 1 | 47k | R | Resistor_SMD:R_0603_1608Metric_Pad0.98x0.95mm_HandSolder | Resistor
R202, | 1 | 330 | R | Resistor_SMD:R_0603_1608Metric_Pad0.98x0.95mm_HandSolder | Resistor
R203, R204, | 2 | 10k NB | R | Resistor_SMD:R_0603_1608Metric_Pad0.98x0.95mm_HandSolder | Resistor
SW201, | 1 | SKRKAEE020 | SW_Push | Button_Switch_SMD:SW_Push_SPST_NO_Alps_SKRK | Push button switch, generic, two pins
SW202, | 1 | A6H-8101 | SW_DIP_x08 | Button_Switch_SMD:SW_DIP_SPSTx08_Slide_Omron_A6H-8101_W6.15mm_P1.27mm | 8x DIP Switch, Single Pole Single Throw (SPST) switch, small symbol
X201, | 1 | ESQ-104-14-G-D | Conn_02x04_Counter_Clockwise | Connector_PinSocket_2.54mm:PinSocket_2x04_P2.54mm_Vertical | Generic connector, double row, 02x04, counter clockwise pin numbering scheme (similar to DIP packge numbering), script generated (kicad-library-utils/schlib/autogen/connector/)
X202, | 1 | Conn_02x03_Counter_Clockwise | Conn_02x03_Counter_Clockwise | Connector_PinHeader_2.54mm:PinHeader_2x03_P2.54mm_Vertical | Generic connector, double row, 02x03, counter clockwise pin numbering scheme (similar to DIP packge numbering), script generated (kicad-library-utils/schlib/autogen/connector/)
X203, | 1 | Conn_01x03 | Conn_01x03 | Connector_PinHeader_2.54mm:PinHeader_1x03_P2.54mm_Vertical | Generic connector, single row, 01x03, script generated (kicad-library-utils/schlib/autogen/connector/)
X301, | 1 | Molex Nano-Fit 105314-1114 | Conn_02x07_Top_Bottom | Connector_Molex:Molex_Nano-Fit_105314-xx14_2x07_P2.50mm_Horizontal | Generic connector, double row, 02x07, top/bottom pin numbering scheme (row 1: 1...pins_per_row, row2: pins_per_row+1 ... num_pins), script generated (kicad-library-utils/schlib/autogen/connector/)
Y201, | 1 | 9HT11-32.768KDZF-T | Crystal | Crystal:Crystal_SMD_TXC_9HT11-2Pin_2.0x1.2mm_HandSoldering | Two pin crystal

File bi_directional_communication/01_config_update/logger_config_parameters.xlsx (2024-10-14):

Parameter name (in json syntax) | example value | Long name | Explanation | Basic logger | Datatype on modular logger | Parameter not in DB | Parameter in DB - Entity | Parameter in DB - Attribute
{
"logger_id" | 5, | Logger ID | Unique ID of this logger | used | uint16 |  | Logger | logger_id
"operation_mode" | "profiling_Travemuende", | Operation mode | (only needed as meta data) | no | char(45) |  | Logger | operation_mode
"fw_version" | "base", | Firmware version |  | no | char(100) |  | Logger | fw_version
"num_sensors" | 2 | Number of sensors (attached to logger) | Generated automatically | no | uint8 | implicit | LoggerContainsSensor
"wifi" | [ |  |  |  |  | x
{
"ssid" | "SSID1", | Wifi SSID |  | used | char(15) | x
"passw" | "***" | Wifi password |  | used | char(16) | x
},
{
"ssid" | "SSID2", |  | modular logger allows several sets of wifi credentials, which | no second set of wifi |  | x
"passw" | "***" |  | are checked in the given order |  |  | x
}
],
"config_update_periode" | 3600, | Config update periode | interval [s] when to check for update | hard coded | uint32 | x
"status_upload_periode" | 3600, | Status upload periode | interval [s] when to upload new status | hard coded | uint32 | x
"sample_periode" | 2 | Sample periode | interval [s] in which to sample (if underwater) | hard coded | uint16 | x
"sample_cast_enable" | 0, | Sample cast enable | if enabled, logger measures with different periode if down or upcast is detected | no | boolean | x
"sample_cast_periode" | 1, | Sample cast periode | interval [s] in which to sample, if logger has detected a cast | no | uint8 | x
"cast_det_sensor" | 23, | Cast detection sensor | ID of sensor for detecting a cast (usually pressure) | no | uint16 | x
"cast_det_sensor_threshold" | 50, | Cast detection sensor threshold | a cast is detected, if this threshold is exceeded by 'difference in sensor reading during 1s', so usually [mbar/s] | no | float | x
"wet_det_sensor" | 23, | Wet detection sensor | ID of sensor for detecting the beginning of a dive | hard coded | uint16 | x
"wet_det_periode" | 15, | wet detection periode | interval [s] when to check if immersed | used | uint16 | x
"wet_det_threshold" | 1050, | wet detection threshold | if reading of wet_det_sensor > this threshold, an immersion is detected | used | float | x
"dry_det_sensor" | 23, | dry detection sensor | ID of sensor for detecting the end of a dive | no | uint16 | x
"dry_det_threshold" | 1050, | dry detection threshold | if reading of dry_det_sensor < this threshold, an emersion is detected | no | float | x
"dry_det_verify_delay" | 5, | dry detection verify delay | time [s] at the end of a dive to continue measureing and check for reimmersion | no | uint16 | x
"data_upload_retry_periode" | 300, | data upload retry periode | time [s] to wait until retry, if a data trasmission failed | hard coded | uint16 | x
"deckunit_id" | 6, | Deckunit ID | (only needed as meta data), ID of primary deck box for this logger | used | uint16 |  | DeckUnit | deck_unit_id
"platform_id" | 7, | Platform ID | (only needed as meta data), ID of platform this logger is deployed on | used | uint16 |  | Platform | platform_id
"vessel_id" | 7, | Vessel ID | (only needed as meta data) | used | uint16 |  | Vessel | vessel_id
"vessel_name" | "Paula", | Vessel name | (only needed as meta data) | used | char(45) |  | Vessel | name
"deployment_contact_id" | 1, | Deployment contact ID | (only needed as meta data) | used | uint16 |  | Contact | contact_id
"contact_first_name" | "Peter", | Contact first name | (only needed as meta data) | used | char(45) |  | Contact | first_name
"contact_last_name" | Petersen", | Contact last name | (only needed as meta data) | used | char(45) |  | Contact | last_name
"sensors" | [ |  | Information on all connected sensors:
{ |  |  | Information on one specific sensor:
"sensor_id" | 11, | Sensor ID |  | used | uint16 |  | Sensor | sensor_id
"sample_periode_multiplier" | 1, | Sample periode multiplier | measuring period of this sensor = sample_periode * sample_periode_multiplier | no | uint8 | x
"sample_cast_periode_multiplier" | 1, | Sample cast periode multiplier | measuring period of this sensor during cast = sample_periode * sample_cast_periode_multiplier | no | uint8 | x
"bus_address" | 2, | Bus address | Address of the interfaceboard of this sensor in the I2C bus | no | uint8 |  | LoggerContainsSensor | bus_address
"calib_coeff" | { | Calibration coefficients |  | used | 10
"0" | -1.128306E+1, |  | 0 to 10 calib coefficients can be given to one sensor | used | float |  | CalibrationCoefficient | value
"1" | 233434534 |  |  | used | float |  | CalibrationCoefficient | value
},
"sensor_type" | { |  | All information on the type of this sensor: |  | 32 |  | SensorType
"sensor_type_id" | 7, | Sensor type ID | (only needed as meta data) | used | uint8 |  | SensorType | sensor_type_id
"parameter" | "temperature", | Parameter | (only needed as meta data) | used | char(45) |  | SensorType | parameter
"long_name" | "sea_water_temperature", | Long name | (only needed as meta data) | used | char(100) |  | SensorType | long_name
"unit" | "degC", | Unit | (only needed as meta data) | used | char(45) |  | Unit | unit
"manufacturer" | "AML", | Manufacturer | (only needed as meta data) | used | char(45) |  | SensorType | manufacturer
"model" | "XchangeCT", | Model | (only needed as meta data) | used | char(45) |  | SensorType | model
"serial_number" | "123456", | Serial number | (only needed as meta data) | used | char(45) |  | Sensor | serial_number
"parameter_no" | 1, | Parameter no | Shall be used if a sensor can measure more than one parameter (to set the order of the parameters) | no | uint8 |  | SensorType | parameter_no
"accuracy" | 0.01, | Accurancy | (only needed as meta data) | used | float |  | SensorType | accuracy
"resolution" | 0.001 | Resolution | (only needed as meta data) | used | float |  | SensorType | resolution
}
},
{
"sensor_id" | 23, | s. above
"sample_periode_multiplier" | 2,
"sample_periode_multiplier_upcast" | 1,
"bus_address" | 3,
"calib_coeff" | {
"0" | 231231,
"1" | 534
},
"sensor_type" | {
"sensor_type_id" | 10,
"parameter" | "pressure",
"long_name" | "sea_water_temperature",
"unit" | "mbar",
"manufacturer" | "keller",
"model" | "series_20",
"serial_number" | "234567",
"parameter_no" | 1,
"accuracy" | 0.1,
"resolution" | 0.01
}
}
]
}

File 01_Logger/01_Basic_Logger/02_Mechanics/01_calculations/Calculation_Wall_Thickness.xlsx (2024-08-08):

Variable | Physical Quantity | Value | Unit | Value | Unit | Value | Unit | Value | Unit | Value | Unit | Value | Unit | Value | Unit
 |  | HyFiVe |  |  |  |  |  |  |  | Zur Plausibilisierung:
Case |  | Cast Acryl |  | Alu |  | Steel |  | POM |  | Blue Rob Arclic Cylinder |  | Blue Rob End Cap |  | Modul Meeresforsch.-tech.
Design Definitions
D_o | Outer Diameter | 0.08 | m | 0.08 | m | 0.08 | m | 0.08 | m | 0.0762 | m | 0.0762 | m | 0.08 | m
 | Working depth | 300 | m | 300 | m | 300 | m | 300 | m | 120 | m | 400 | m | 500 | m
s | Safety factor | 1.5 | 1 | 1.5 | 1 | 1.5 | 1 | 1.5 | 1 | 1.5 | 1 | 1.5 | 1 | 1.5 | 1
p_e | Design pressure | 4500000 | Pa | 4500000 | Pa | 4500000 | Pa | 4500000 | Pa | 1800000 | Pa | 6000000 | Pa | 7500000 | Pa
Material constants
 | Material | Cast Acryl |  | Aluminium 6061-T6 |  | Stainless steel 316 |  | POM |  | Cast Acryl |  | Aluminium 6061-T6 |  | Aluminium
E | Modulus of elasticity | 3000000000 | Pa | 69000000000 | Pa | 193000000000 | Pa | 2940000000 | Pa | 3000000000 | Pa | 69000000000 | Pa | 70000000000 | Pa
my | Possion`s ratio (Querkontraktionszahl) | 0.37 | 1 | 0.33 | 1 | 0.29 | 1 | 0.44 | 1 | 0.37 | 1 | 0.33 | 1 | 0.34 | 1
Sy | tensile yield strength/ Streckgrenze | 64800000 | Pa | 275000000 | Pa | 240000000 | Pa | 67000000 | Pa | 64800000 | Pa | 275000000 | Pa | 20000000 | Pa
 | Source | http://www.matweb.com/search/datasheet.aspx?bassnum=O1303&ckck=1 |  | http://asm.matweb.com/search/SpecificMaterial.asp?bassnum=ma6061t6 |  | http://www.matweb.com/search/DataSheet.aspx?MatGUID=dfced4f11d63459e8ef8733d1c7c1ad2&ckck=1 |  | https://polymerdatabase.com/Commercial%20Polymers/Polyacetal.html, https://polymerdatabase.com/polymer%20physics/Poisson%20Table2.html, https://www.azom.com/article.aspx?ArticleID=762, https://designerdata.nl/materials/plastics/thermo-plastics/polyoxymethylene-(hom.) |  | http://www.matweb.com/search/datasheet.aspx?bassnum=O1303&ckck=1 |  | http://asm.matweb.com/search/SpecificMaterial.asp?bassnum=ma6061t6
Calculation of min. wall thickness
Failure Mode: Elastic buckling
t_min_el | min. wall thickness | 6.9 | mm | 2.5 | mm | 1.8 | mm | 6.8 | mm | 4.9 | mm | 2.6 | mm | 2.9 | mm
t_chosen | wall thickness chosen | 0.007 | m | 0.003 | m | 0.003 | m | 0.007 | m | 0.007 | m | 0.003 | m | 0.0035 | m
Checking Failure Mode: Inelastic buckling
sigma_max | max stress at tube inner surface | 28180039.14 |  | 62337662.34 |  | 62337662.34 |  | 28180039.14 |  | 10788183.32 |  | 79322950.82 |  | 89635854.34
 | Is Inelastic buckling a problem? | no problem |  | no problem |  | no problem |  | no problem |  | no problem |  | no problem |  | problem
Endcaps
t_cap_min | Minimum thickness of end caps | 9.8 | mm | 5.3 | mm | 5.6 | mm | 9.7 | mm | 5.8 | mm | 5.8 | mm | 25.0 | mm
t_cap_chosen | Chosen thickness of end caps | 12 | mm
 | Zur Plausibilisierung:
 | Design using the given diagramms
 | t/D_o |  |  |  |  |  |  |  |  | 0.09186351706
 | Inelastic Yielding
 | P_collapse_IY/Sy (read from diagramm) |  |  |  |  |  |  |  |  | 0.17
 | P_collapse_IY |  |  |  |  |  |  |  |  | 11016000 | pa
 | Depth |  |  |  |  |  |  |  |  | 1101.6 | m
 | Elastic Buckling
 | P_collapse_EB/E*10^3 (read from diagramm) |  |  |  |  |  |  |  |  | 1.425
 | P_collapse_EB |  |  |  |  |  |  |  |  | 4275000 | pa
 | Depth |  |  |  |  |  |  |  |  | 427.5
 | Diagramme liefern gleiche Werte
 | Englisch-Deutsch
 | (tensile) yield strength | Streckgrenze |  |  |  |  |  |  |  | Streckgrenze
 | ultimate tensile strength | Zugfestigkeit |  |  |  |  |  |  |  | Zugfestigkeit

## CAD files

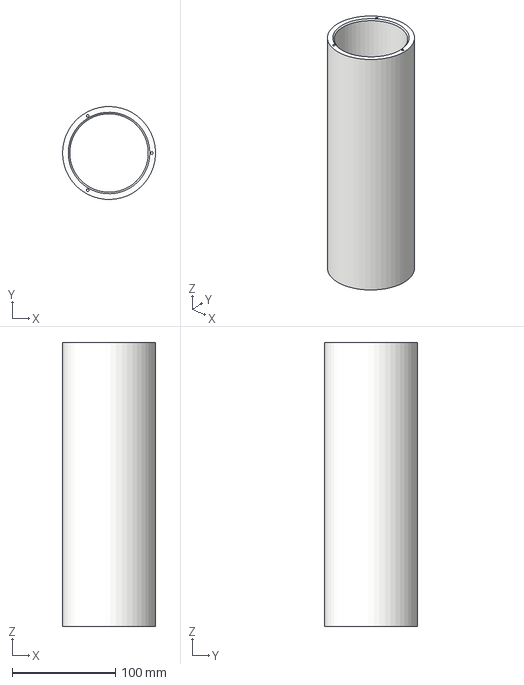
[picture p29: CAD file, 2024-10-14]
01_Logger/01_Basic_Logger/02_Mechanics/02_pressure_housing/02_cylinder/Logger_cylinder.step
89.9 x 90.0 x 275.0 mm

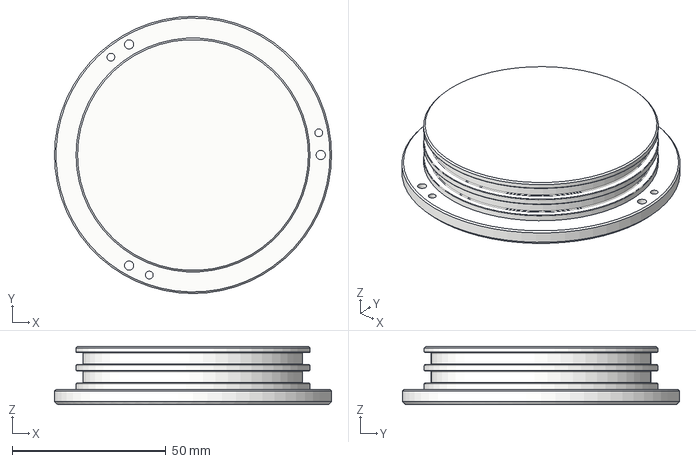
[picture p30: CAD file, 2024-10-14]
01_Logger/01_Basic_Logger/02_Mechanics/02_pressure_housing/03_endcaps/end_cap_blank.step
90.0 x 90.0 x 19.0 mm

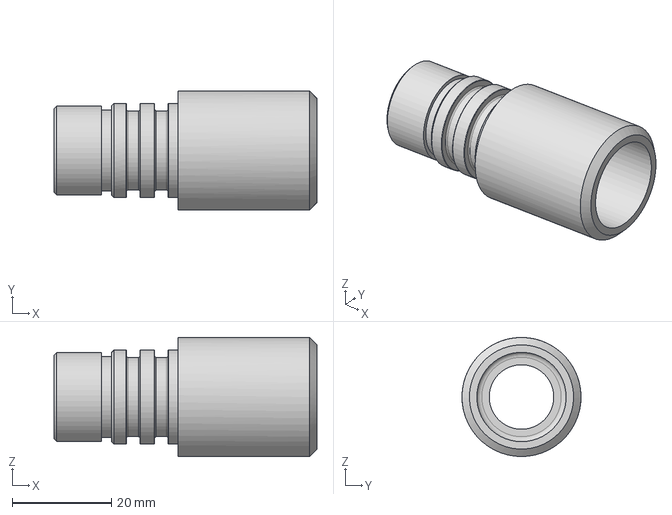
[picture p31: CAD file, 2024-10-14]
01_Logger/01_Basic_Logger/02_Mechanics/02_pressure_housing/04_penetrators/penetrator_sensor_Atlas_K1_0.step
53.0 x 24.0 x 24.0 mm

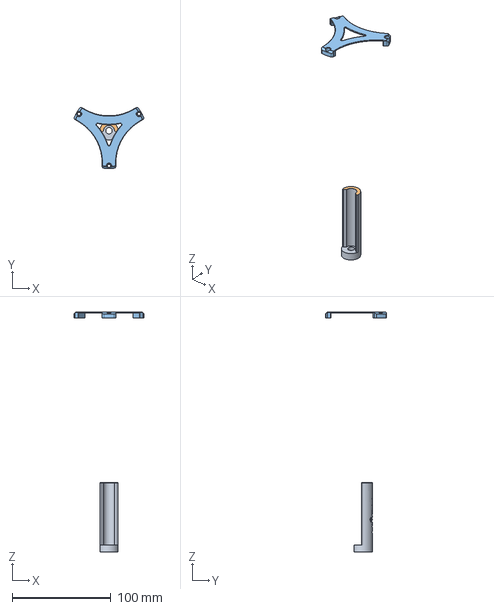
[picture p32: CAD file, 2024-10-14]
01_Logger/01_Basic_Logger/02_Mechanics/03_electronic_mounting/logger_mounting_battery_base.step
70.3 x 61.7 x 242.5 mm
mounting_electronics_foot
logger_mounting_battery

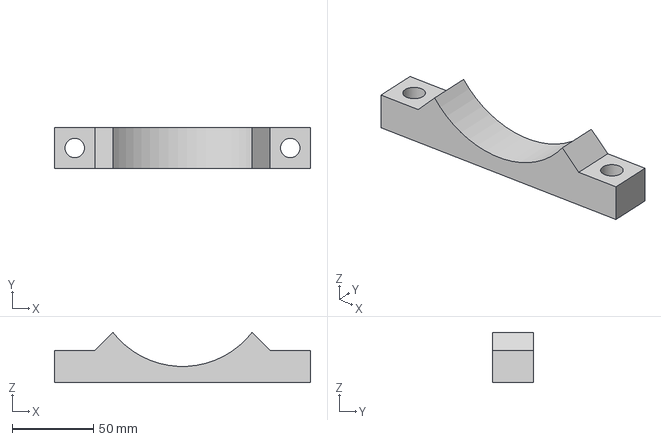
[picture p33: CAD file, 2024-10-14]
01_Logger/01_Basic_Logger/02_Mechanics/04_otter_board_mounting/01_main_parts/support.step
158.0 x 25.0 x 31.1 mm

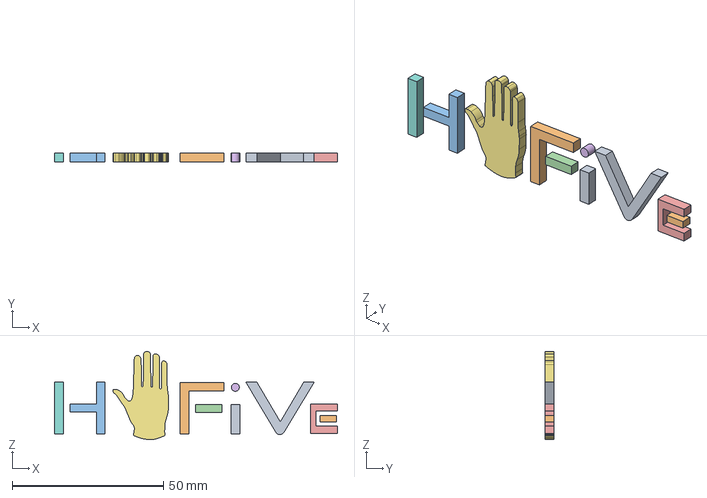
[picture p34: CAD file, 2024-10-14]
01_Logger/01_Basic_Logger/02_Mechanics/04_otter_board_mounting/02_small_components/inlay_back_series_letters.step
93.6 x 3.00 x 29.2 mm

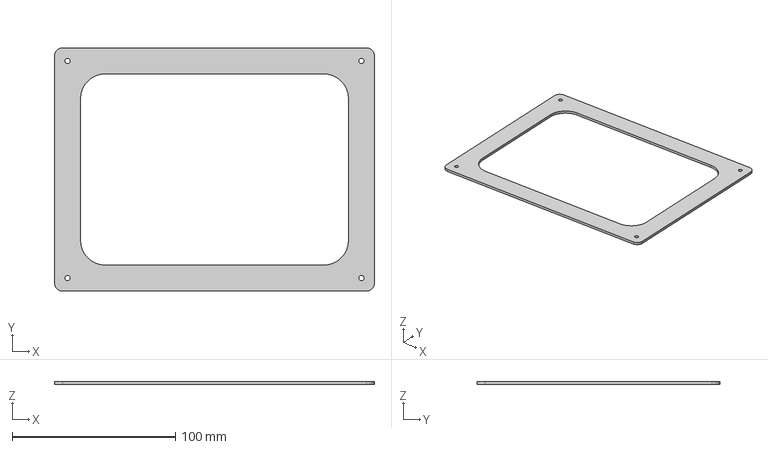
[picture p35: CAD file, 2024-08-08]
01_Logger/01_Basic_Logger/02_Mechanics/04_otter_board_mounting/03_stencils/stencil_drilling_on_vessel.step
196.0 x 149.0 x 2.00 mm

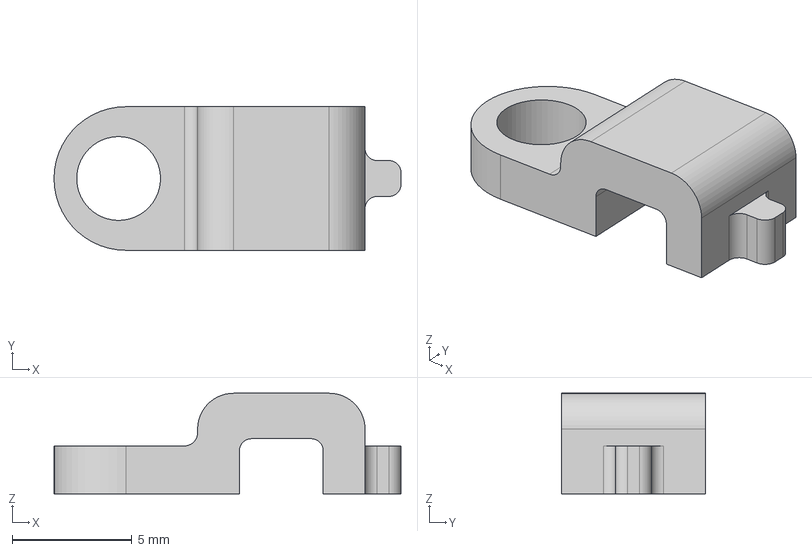
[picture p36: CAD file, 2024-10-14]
01_Logger/02_Modular_Logger/02_Mechanics/01_electronic_mounting/logger_mounting_reed_switch.step
14.5 x 6.00 x 4.20 mm

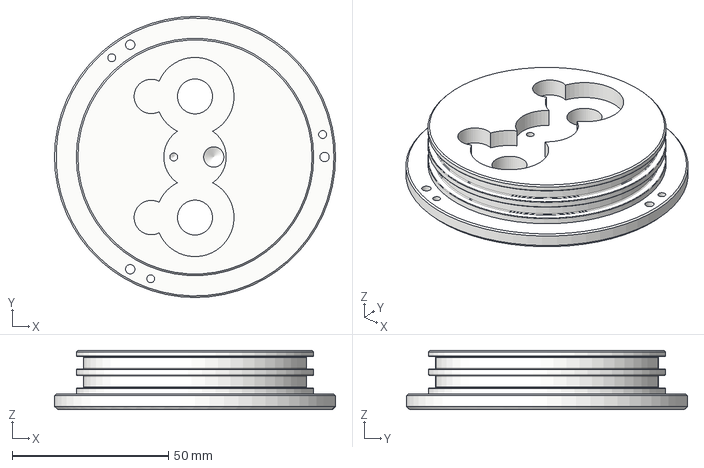
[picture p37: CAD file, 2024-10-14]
01_Logger/02_Modular_Logger/02_Mechanics/01_pressure_housing/01_end_caps/End_cap_drilling_charging.step
90.0 x 90.0 x 19.0 mm

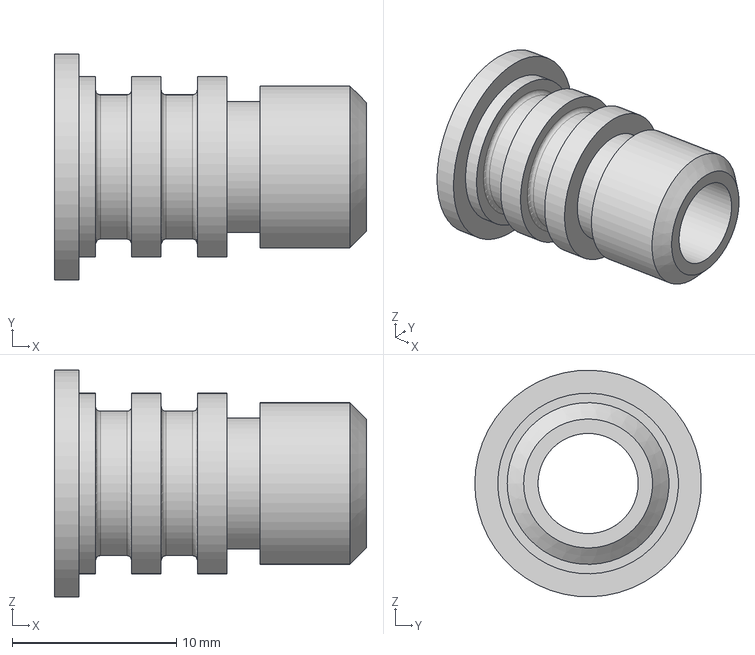
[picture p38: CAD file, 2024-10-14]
01_Logger/02_Modular_Logger/02_Mechanics/01_pressure_housing/02_penetrators/penetrator_LED.step
19.0 x 13.8 x 13.8 mm

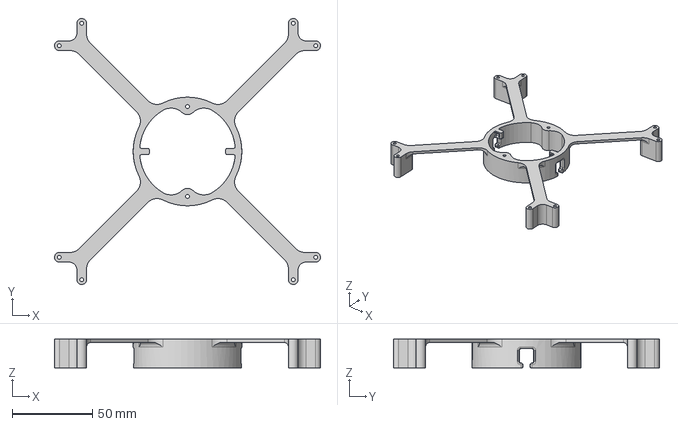
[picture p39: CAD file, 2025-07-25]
02_Deckbox/01_Hardware/01_mechanic/01_internal_mounting/mounting_antennas/Deckbox_v2_mounting_antennas_level_2.step
166.0 x 166.0 x 18.0 mm

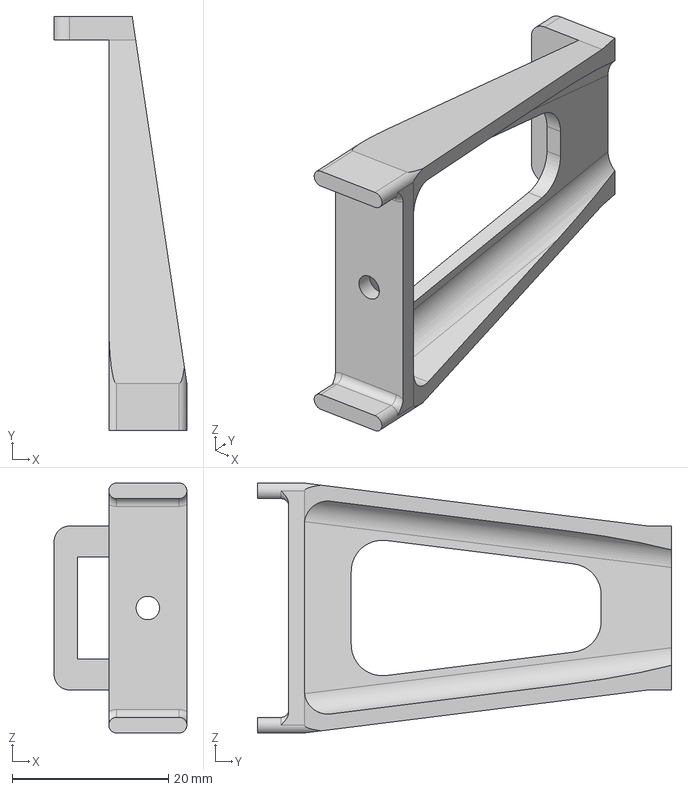
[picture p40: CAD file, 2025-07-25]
02_Deckbox/01_Hardware/01_mechanic/01_internal_mounting/mounting_electronics/DC_DC_Clamp_v2.step
17.0 x 53.0 x 32.0 mm

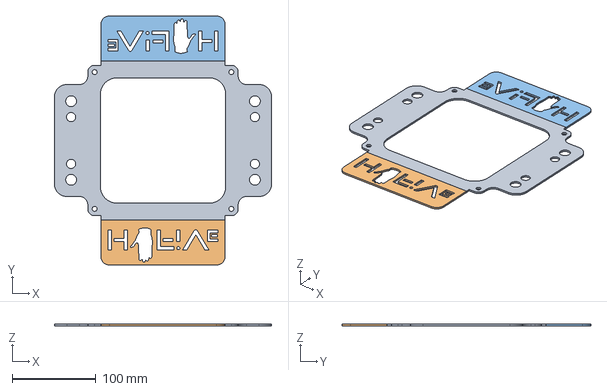
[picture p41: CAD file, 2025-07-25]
02_Deckbox/01_Hardware/01_mechanic/02_external_mounting/Deckbox_v2_external_mounting_flat.step
260.0 x 298.0 x 2.00 mm

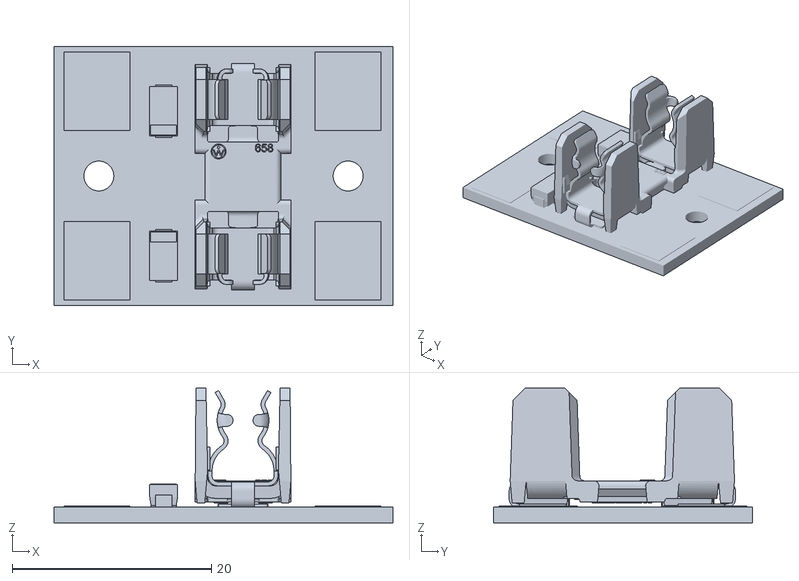
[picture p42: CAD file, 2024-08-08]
02_Deckbox/01_Hardware/02_electronic/PCB_DC_PowerDistrubution/DeckunitV1 v1.stl
34.0 x 26.0 x 13.5

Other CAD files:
01_Logger/01_Basic_Logger/02_Mechanics/02_pressure_housing/03_endcaps/end_cap_drillings_sensors.step
01_Logger/01_Basic_Logger/02_Mechanics/03_electronic_mounting/logger_mounting_battery_top.step
01_Logger/01_Basic_Logger/02_Mechanics/04_otter_board_mounting/01_main_parts/pipe_watercutted.step
01_Logger/01_Basic_Logger/02_Mechanics/04_otter_board_mounting/02_small_components/inlay_back_series.step
01_Logger/01_Basic_Logger/02_Mechanics/02_pressure_housing/02_cylinder/Logger_cylinder.f3d
01_Logger/01_Basic_Logger/02_Mechanics/02_pressure_housing/03_endcaps/end_cap_blank.f3d
01_Logger/01_Basic_Logger/02_Mechanics/02_pressure_housing/03_endcaps/end_cap_drillings_sensors.f3d
01_Logger/01_Basic_Logger/02_Mechanics/02_pressure_housing/04_penetrators/penetrator_sensor_Atlas_K1_0.f3d
01_Logger/01_Basic_Logger/02_Mechanics/03_electronic_mounting/logger_mounting_battery_base.stl
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

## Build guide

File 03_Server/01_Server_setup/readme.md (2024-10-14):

# HyFiVe Server - Setup SFTP, Users, VPN

The server is a virtual machine running Ubuntu 20.04.6 LTS with 4 CPU cores and 8 GB of RAM

## SFTP Server
The SFTP server is used to transfer data between the server and the deck boxes. Therefore a own group is created and the server is installed

```
	sudo addgroup sftprestricted
	sudo apt-get install openssh-server  openssh-sftp-server
```

Configure SFTP Chroot Jail in SFTP Chroot Jail in /etc/ssh/sshd_config:
```
	Match Group sftprestricted
		ChrootDirectory %h
		ForceCommand internal-sftp
		PasswordAuthentication yes
		PubkeyAuthentication yes
		PermitTunnel no
		AllowAgentForwarding no
		AllowTcpForwarding no
		X11Forwarding no
```

## Users

Next to the admin two users are needed for the full functionality of the overall system:

1. mainuser: This user runs all operations on the server, creates all folders and runs the cronjobs
	
	add with ```sudo adduser hyfiveuser```.
	
2. loggermailbox: This user is created for the exchange of files by deck boxes in the field. It has limited access to a mailbox folder which should be created before.
	Within the home directory of the mainuser a folder mailbox is created with the follwoing structure
	```
	mailbox/
		in/
			netcdf/
			status/
		out/
			config/
	```

	A link of this folder is created for the loggermailbox
	```
		ln -s /opt/HyFiVe/mailbox/in/ mailbox
	```
	
	Add the user with
	```
		sudo adduser --no-create-home loggermailbox
		sudo usermod -d /home/hyfiveuser/datain loggermailbox
		sudo usermod -d /opt/HyFiVe/mailbox loggermailbox
		sudo usermod -s /sbin/nologin loggermailbox
		sudo usermod -g sftprestricted loggermailbox
	```

## OpenVPN Server
The OpenVPN server is installed by the admin as follows
```
	sudo apt install openvpn easy-rsa
	sudo make-cadir /etc/openvpn/easy-rsa
	cd /etc/openvpn/easy-rsa 
	./easyrsa init-pki
	./easyrsa build-ca
```
Create Diffie Hellman parameter, a certificat for the OpenVPN server and copie all certificats and keys to /etc/openvpn/
```
	./easyrsa gen-dh
	./easyrsa sign-req server myservername
	cp pki/dh.pem pki/ca.crt pki/issued/myservername.crt pki/private/myservername.key /etc/openvpn/
```
Create certificats and keys for deck boxes
```
	cd ~/openvpn
	/usr/share/easy-rsa/easyrsa gen-req DeckboxXY nopass
	/usr/share/easy-rsa/easyrsa sign-req client DeckboxXY
	cd pki
	zip -j DeckboxXY.zip ./issued/DeckboxXY.crt ./private/DeckboxXY.key ca.crt
```
Modify further settings
```
	sudo cp /usr/share/doc/openvpn/examples/sample-config-files/server.conf.gz /etc/openvpn/myserver.conf.gz
	sudo gzip -d /etc/openvpn/myserver.conf.gz
	ca ca.crt
	cert myservername.crt
	key myservername.key
	dh dh2048.pem
```
Create a ta.key
```
	cd /etc/openvpn
	sudo openvpn --genkey --secret ta.key
```
Umcomment the line ```#net.ipv4.ip_forward=1``` in ```/etc/sysctl.conf``` for IP forwarding and reboot sysctl
```
	sudo sysctl -p /etc/sysctl.conf
```

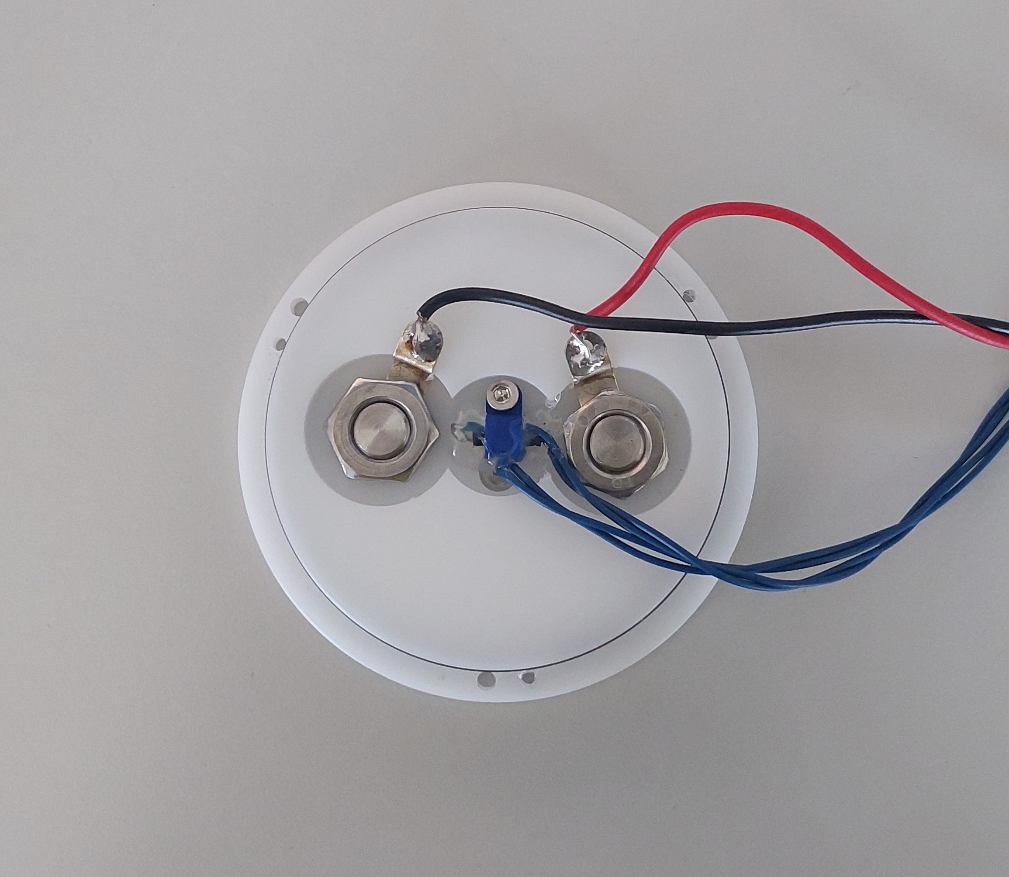
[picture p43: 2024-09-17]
01_Logger/02_Modular_Logger/02_Mechanics/media/end_cap_assembled.jpg

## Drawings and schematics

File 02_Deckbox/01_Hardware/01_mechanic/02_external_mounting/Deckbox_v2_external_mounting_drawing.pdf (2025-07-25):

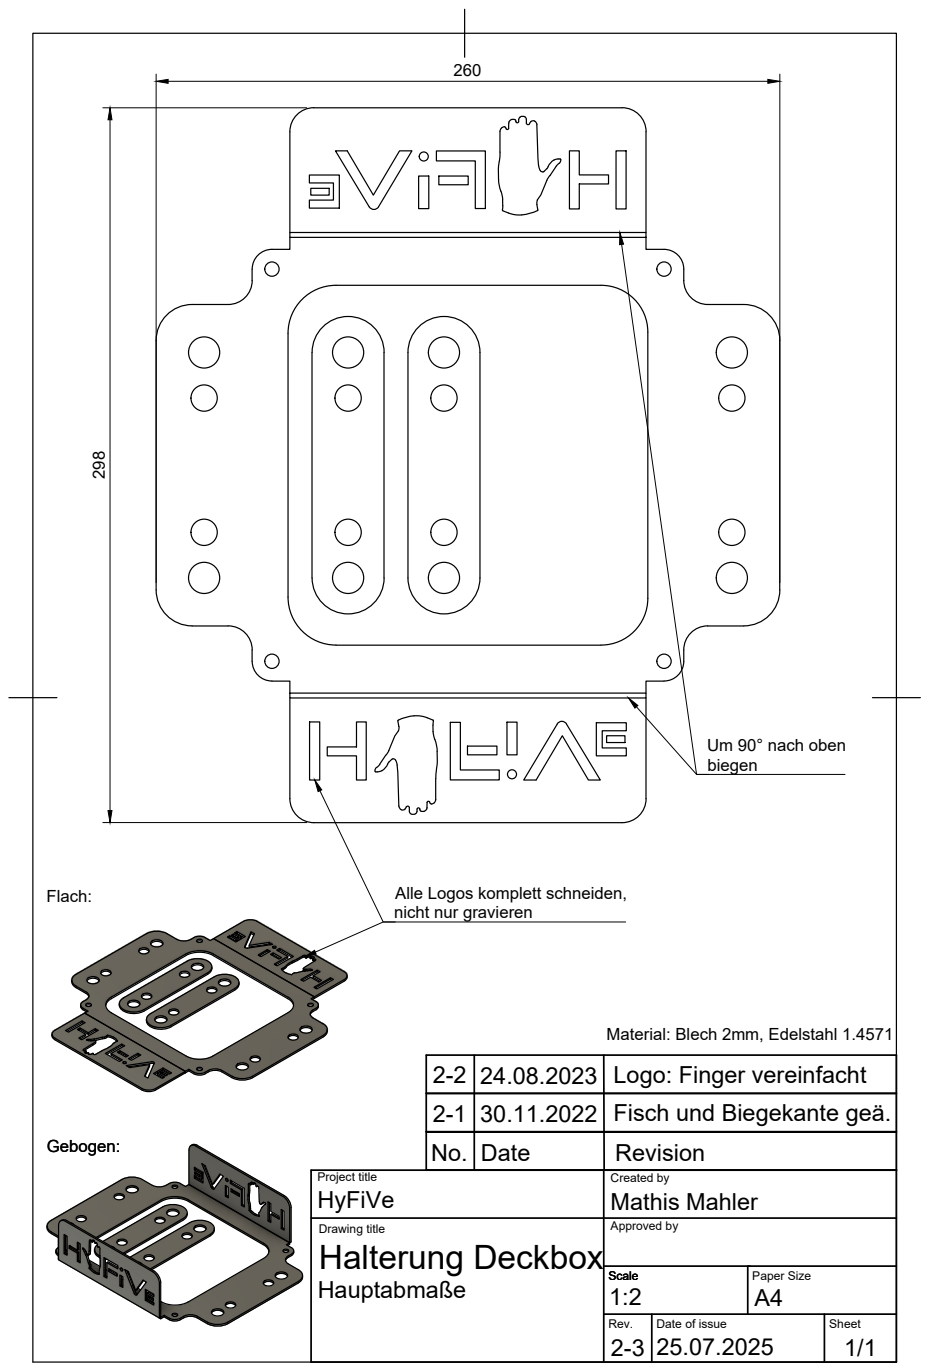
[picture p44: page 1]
Flach: 298

Um 90° nach oben
biegen

Alle Logos komplett schneiden,
nicht nur gravieren

Material: Blech 2mm, Edelstahl 1.4571

2-2 | 24.08.2023 | Logo: Finger vereinfacht
2-1 | 30.11.2022 | Fisch und Biegekante geä.
No. | Date | Revision

Project title HyFiVe | Created by Mathis Mahler

Drawing title Halterung Deckbox Hauptabmaße | Approved by

Scale 1:2 | Paper Size A4

Rev. 2-3 | Date of issue 25.07.2025 | Sheet 1/1

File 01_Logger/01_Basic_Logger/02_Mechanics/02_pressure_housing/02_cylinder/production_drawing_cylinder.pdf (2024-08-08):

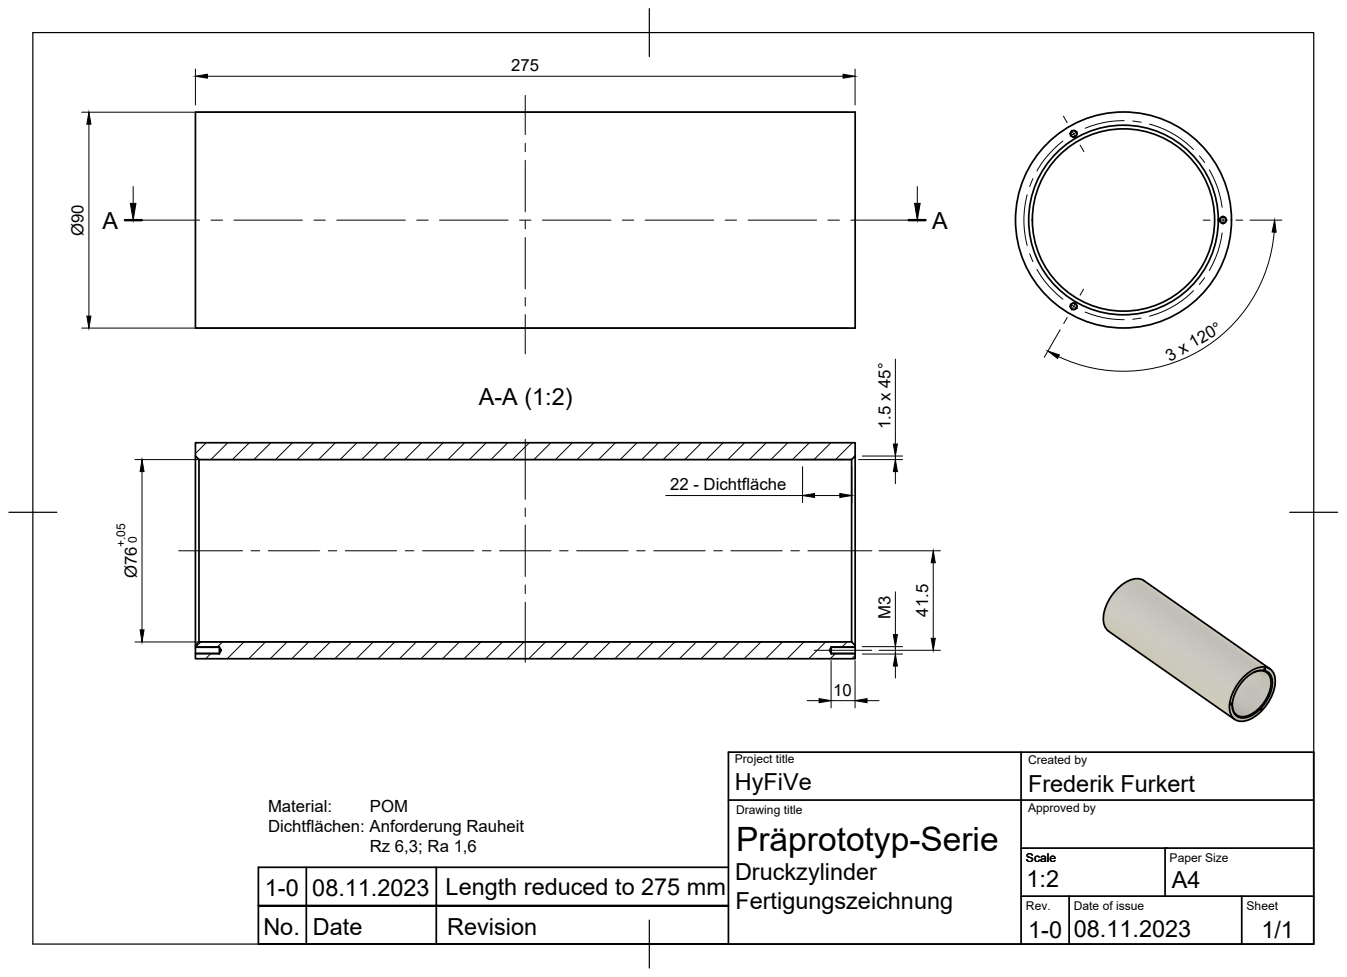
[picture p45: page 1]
Length reduced to 275 mm; 22 - Dichtfläche

Project title HyFiVe | Created by Frederik Furkert

Dichtflächen: Anforderung Rauheit

Drawing title Präprototyp-Serie Druckzylinder Fertigungszeichnung | Approved by

Scale | Paper Size

Rev. | Date of issue | Sheet 1/1

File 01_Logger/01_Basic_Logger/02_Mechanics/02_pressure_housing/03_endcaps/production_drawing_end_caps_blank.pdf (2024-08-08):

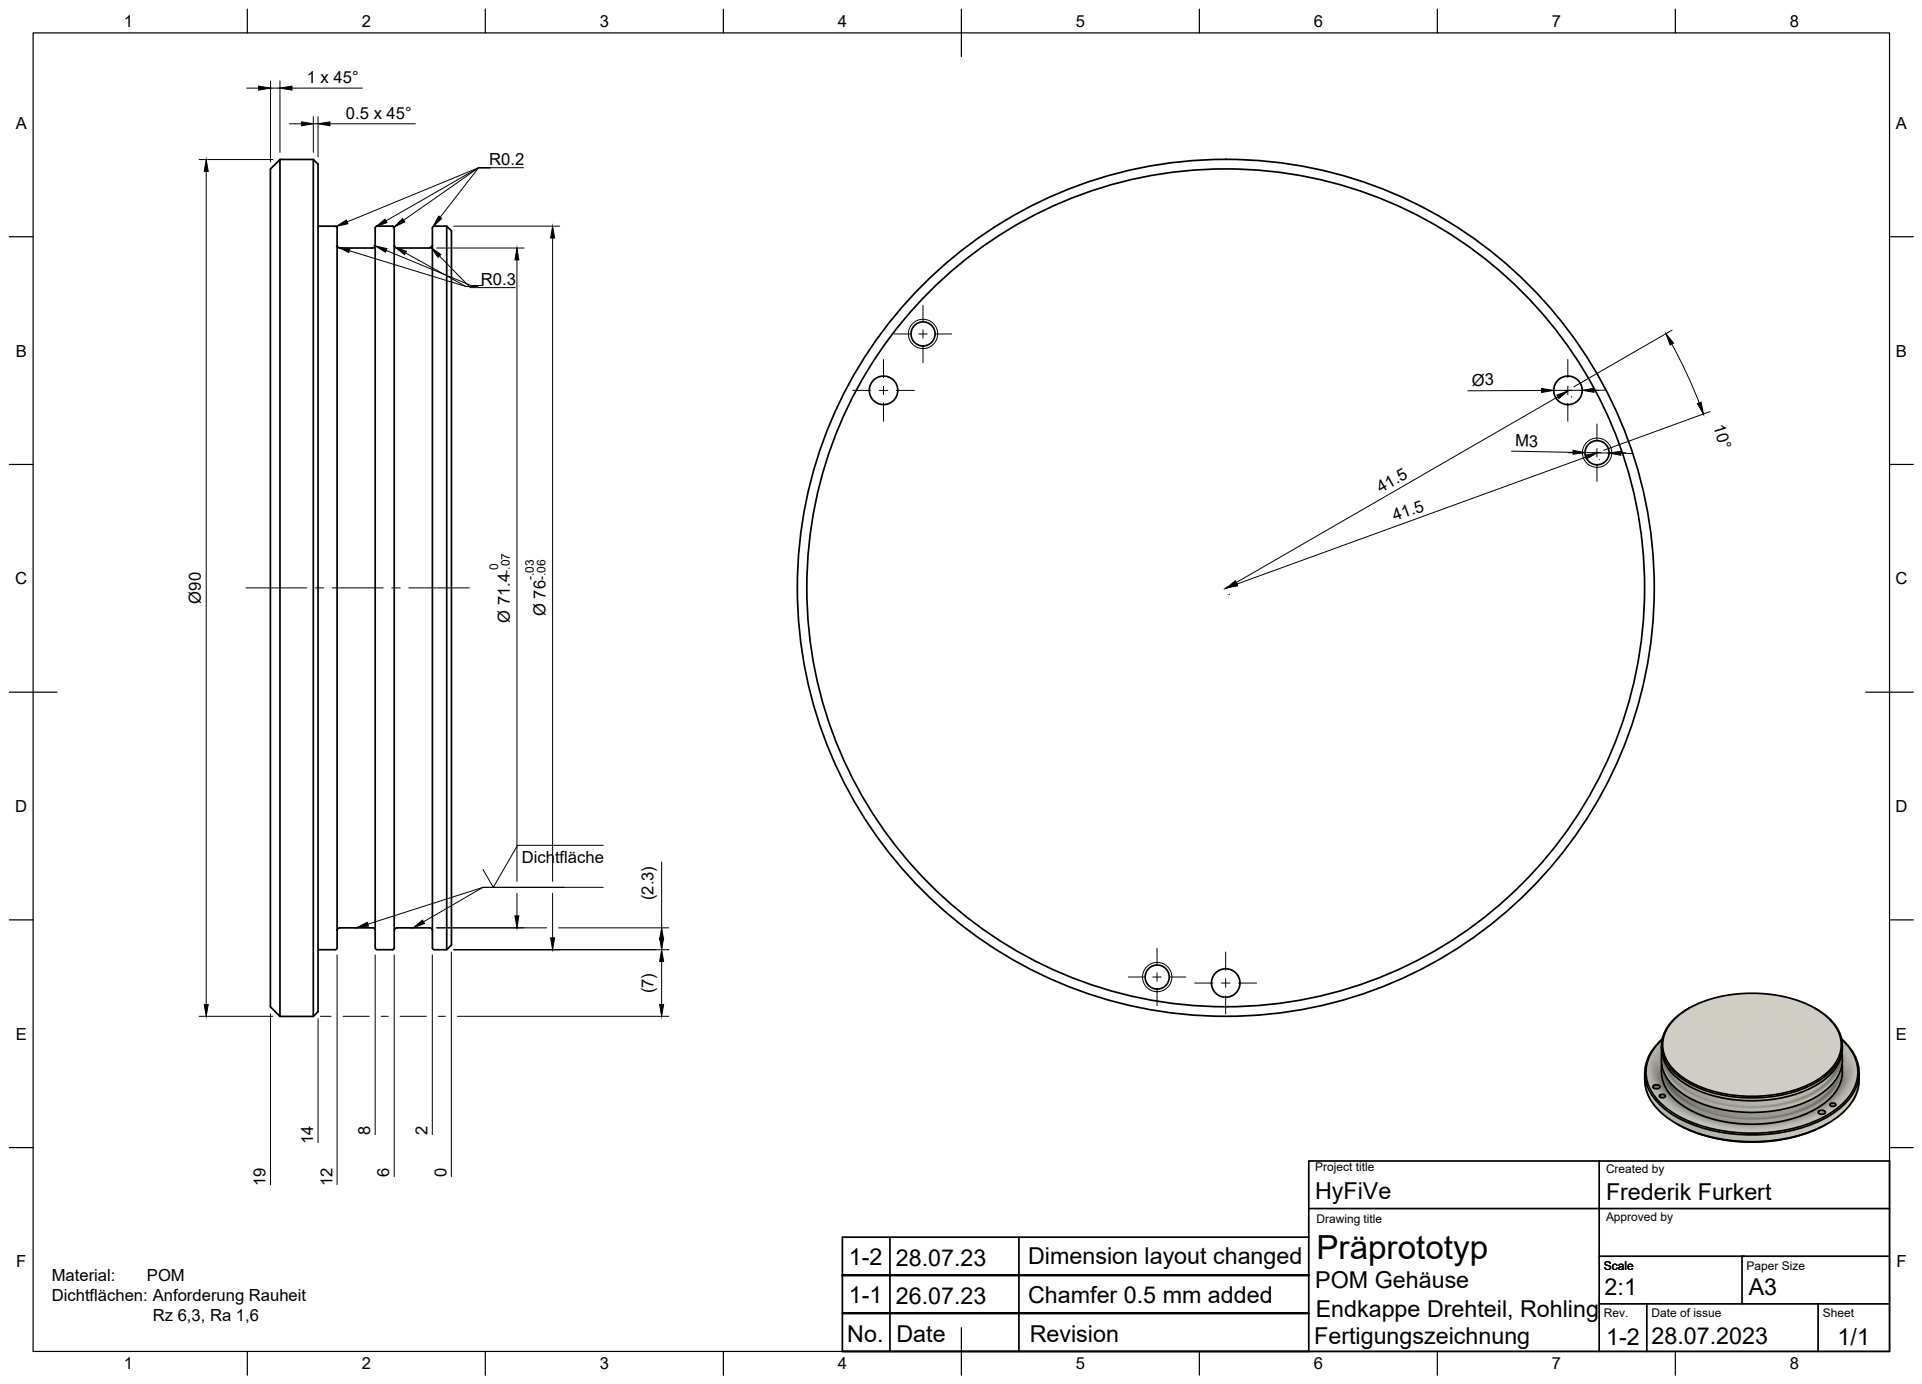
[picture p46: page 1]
Rev.; Date of issue; Sheet

Project title HyFiVe | Created by Frederik Furkert

Drawing title
Präprototyp
POM Gehäuse
Endkappe Drehteil, Rohling
Fertigungszeichnung

Approved by

1-2 | 28.07.23 | Dimension layout changed
1-1 | 26.07.23 | Chamfer 0.5 mm added

Dichtflächen: Anforderung Rauheit

Scale 2:1 | Paper Size A3

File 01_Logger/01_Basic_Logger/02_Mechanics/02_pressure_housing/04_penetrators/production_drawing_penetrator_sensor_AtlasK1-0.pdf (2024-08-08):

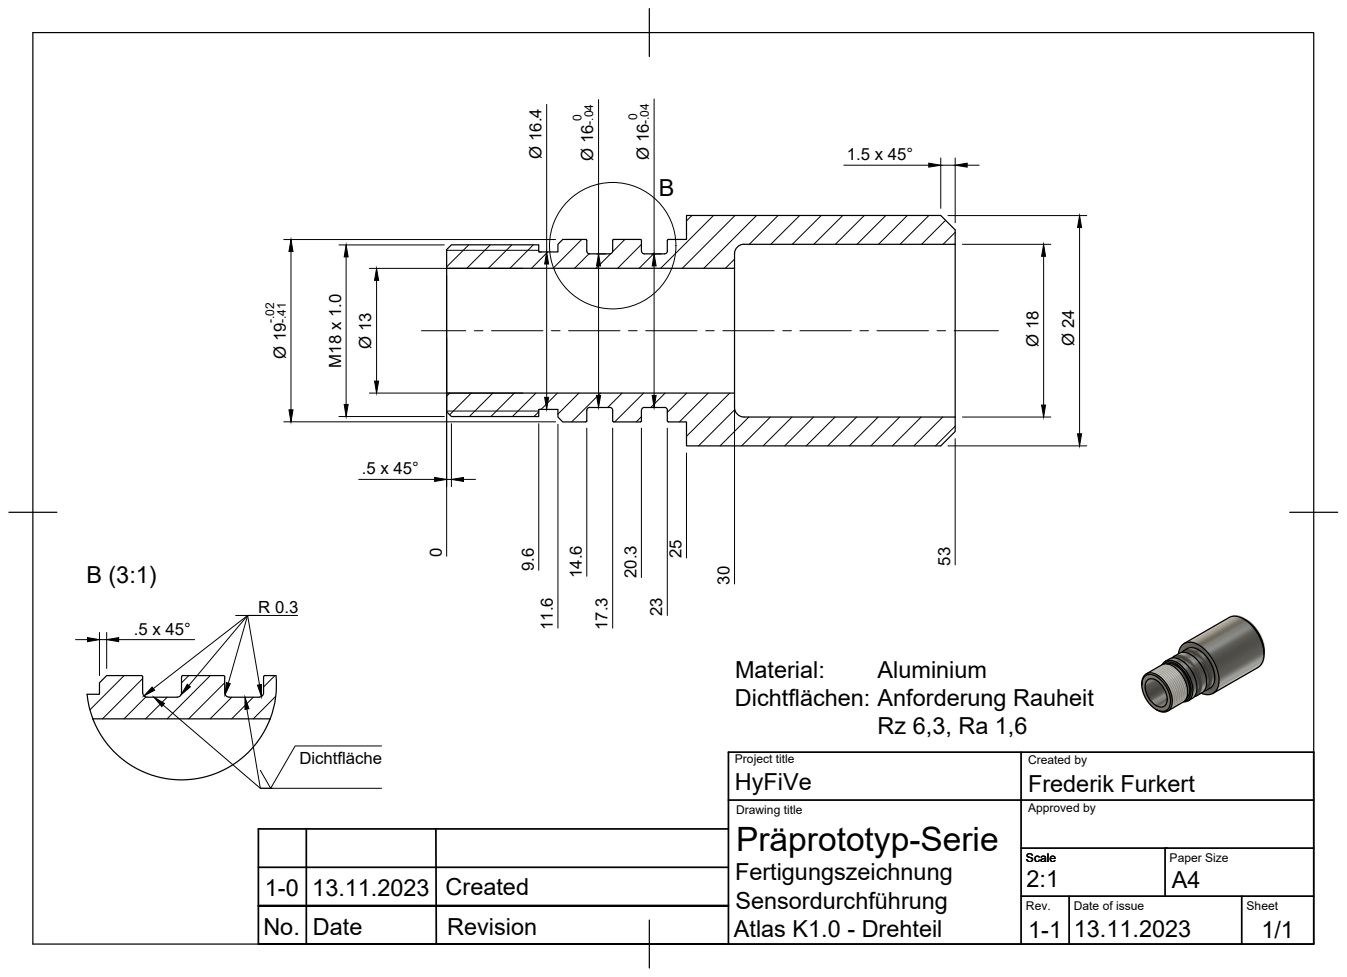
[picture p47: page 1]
Created

Dichtflächen: Anforderung Rauheit

Project title HyFiVe | Created by Frederik Furkert

Drawing title Präprototyp-Serie Fertigungszeichnung Sensordurchführung Atlas K1.0 - Drehteil | Approved by

Scale 2:1 | Paper Size A4

Rev. | Date of issue | Sheet 1/1

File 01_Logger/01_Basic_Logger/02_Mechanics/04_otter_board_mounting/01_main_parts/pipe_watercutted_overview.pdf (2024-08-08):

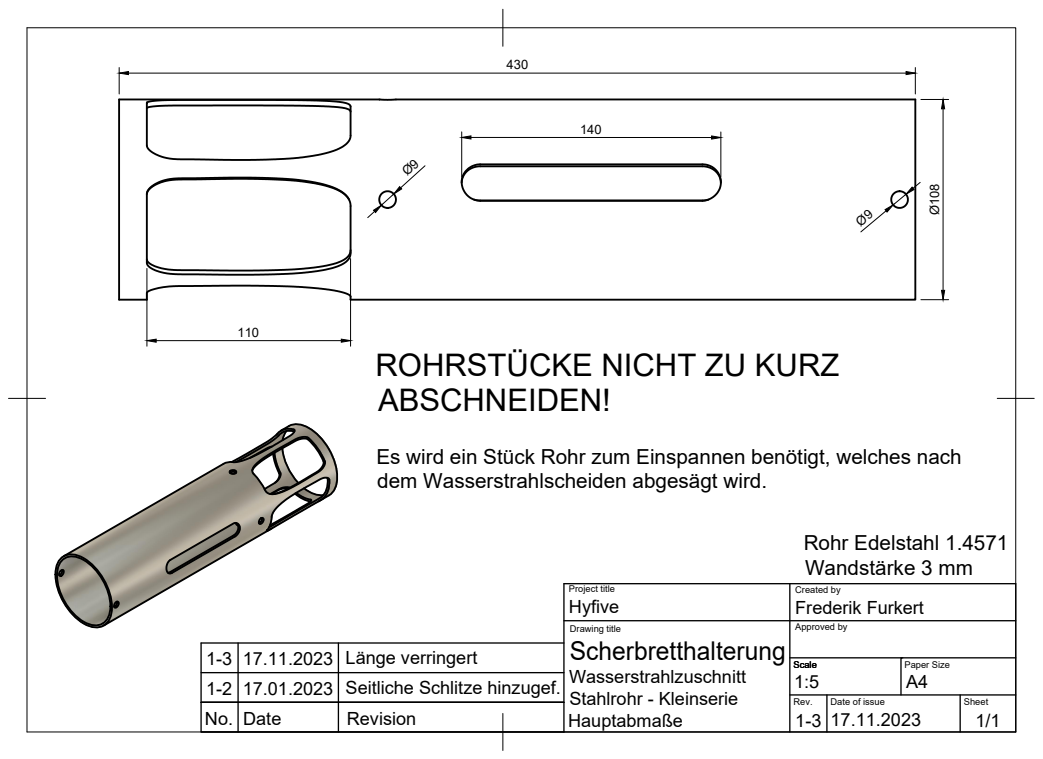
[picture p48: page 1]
Seitliche Schlitze hinzugef.; Länge verringert; Rohr Edelstahl 1.4571 Wandstärke 3 mm

ROHRSTÜCKE NICHT ZU KURZ
ABSCHNEIDEN!

Es wird ein Stück Rohr zum Einspannen benötigt, welches nach
dem Wasserstrahlscheiden abgesägt wird.

Project title Hyfive | Created by Frederik Furkert

Drawing title Scherbretthalterung Wasserstrahlzuschnitt Stahlrohr - Kleinserie Hauptabmaße | Approved by

Scale 1:5 | Paper Size A4

Rev. | Date of issue | Sheet 1/1

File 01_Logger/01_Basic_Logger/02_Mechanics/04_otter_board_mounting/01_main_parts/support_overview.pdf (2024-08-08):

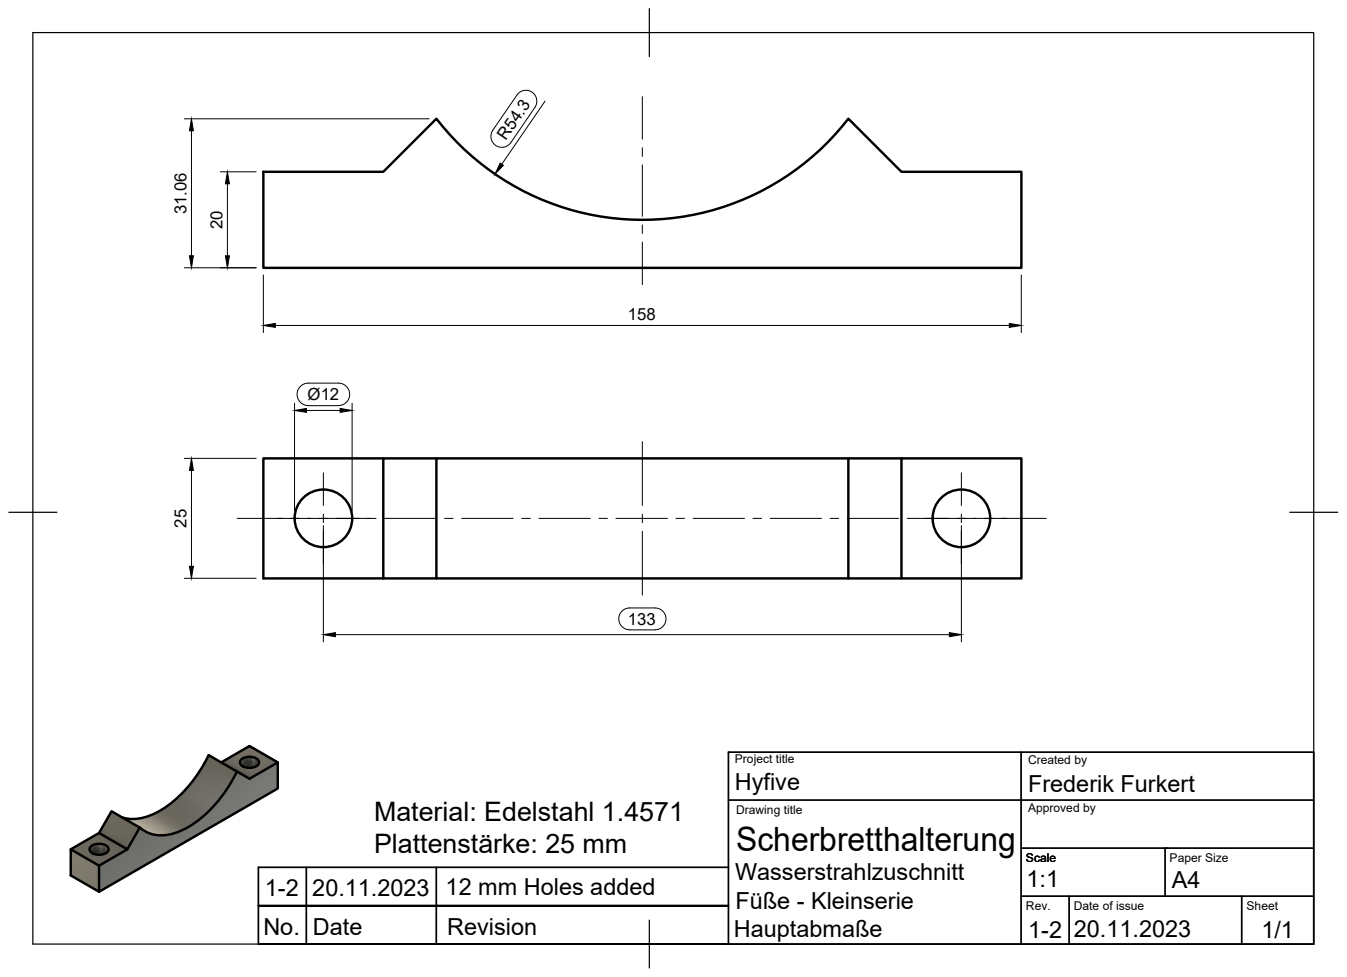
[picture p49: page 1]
12 mm Holes added; Material: Edelstahl 1.4571 Plattenstärke: 25 mm

Project title Hyfive | Created by Frederik Furkert

Drawing title Scherbretthalterung Wasserstrahlzuschnitt Füße - Kleinserie Hauptabmaße | Approved by

Scale 1:1 | Paper Size A4

Rev. | Date of issue | Sheet 1/1

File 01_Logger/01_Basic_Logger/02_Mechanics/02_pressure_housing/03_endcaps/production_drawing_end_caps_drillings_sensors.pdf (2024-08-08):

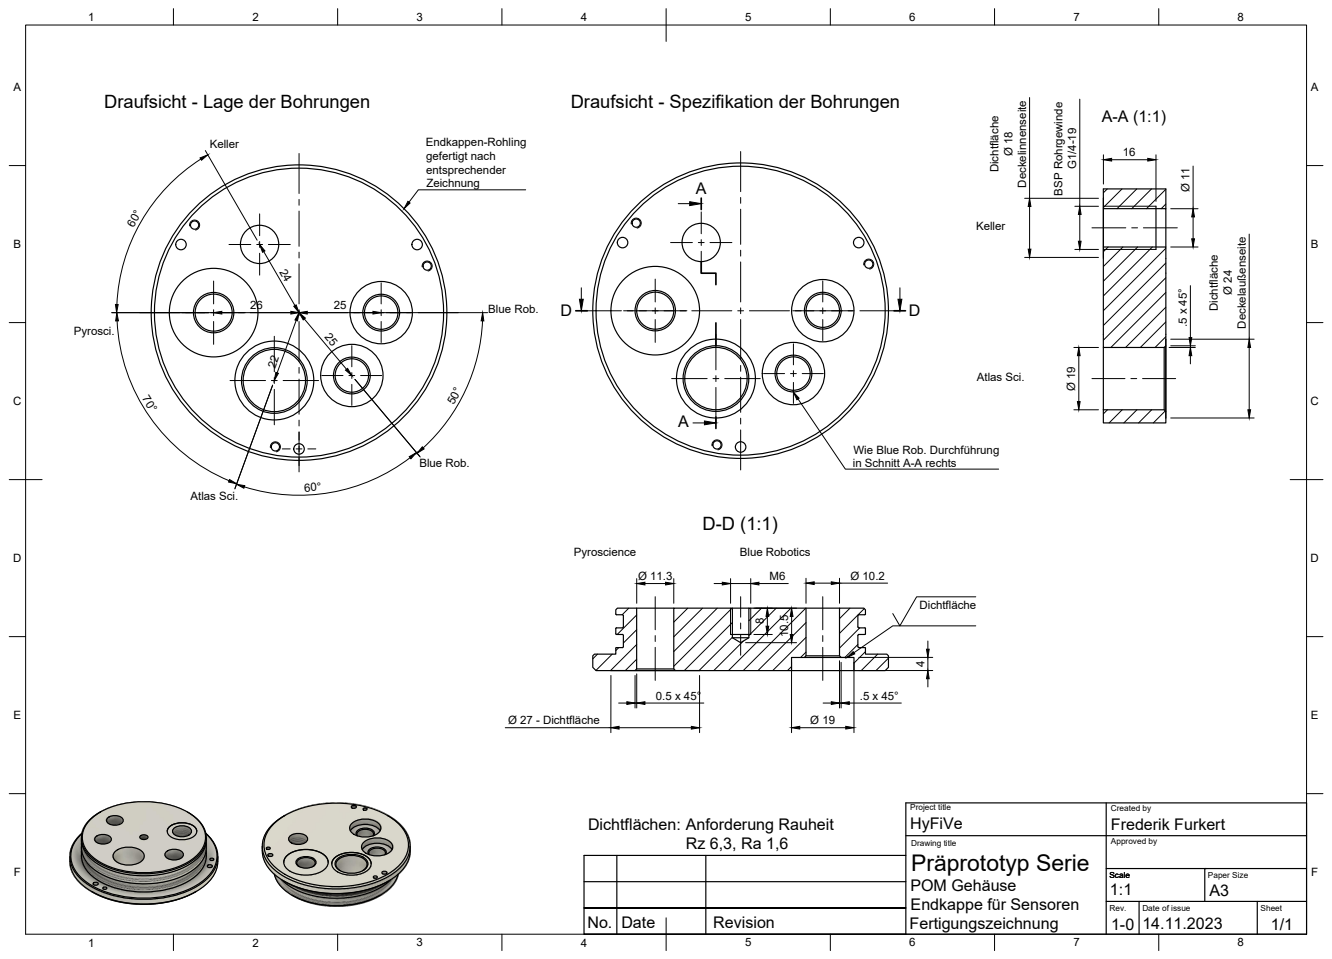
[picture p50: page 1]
Rev.; Date of issue; Sheet; Draufsicht - Lage der Bohrungen; Draufsicht - Spezifikation der Bohrungen; gefertigt nach; Ø 27 - Dichtfläche; Blue Rob.; Atlas Sci.; Pyroscience; Blue Robotics; BSP Rohrgewinde G1/4-19; Dichtfläche Ø 24 Deckelaußenseite; 16 Dichtfläche Ø 18 Deckelinnenseite

Wie Blue Rob. Durchführung
in Schnitt A-A rechts

Project title HyFiVe | Created by Frederik Furkert

Dichtflächen: Anforderung Rauheit

Drawing title
Präprototyp Serie
POM Gehäuse
Endkappe für Sensoren
Fertigungszeichnung

Approved by

Scale 1:1 | Paper Size A3

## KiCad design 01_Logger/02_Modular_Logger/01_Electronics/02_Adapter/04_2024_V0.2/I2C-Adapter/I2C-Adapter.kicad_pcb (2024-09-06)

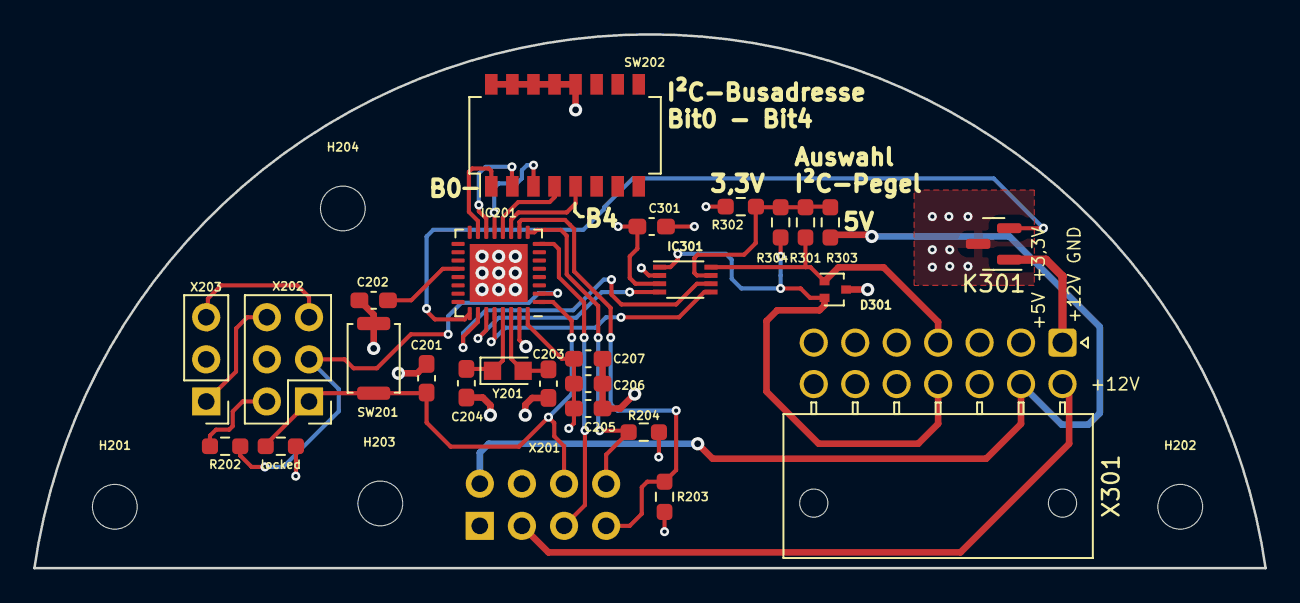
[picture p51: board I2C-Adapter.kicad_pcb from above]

Board: 4 copper layers, 74.2 x 32.2 mm, 31 parts (1 on the bottom side), 28 nets.

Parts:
C201: 1nF; C_0603_1608Metric_Pad1.08x0.95mm_HandSolder
C202: 1µF, <200m ESR; C_0603_1608Metric_Pad1.08x0.95mm_HandSolder
C203, C204: 20pF; C_0603_1608Metric_Pad1.08x0.95mm_HandSolder
C205, C301: 100nF; C_0603_1608Metric_Pad1.08x0.95mm_HandSolder
C206: 1µF; C_0603_1608Metric_Pad1.08x0.95mm_HandSolder
C207: 4,7µF; C_0603_1608Metric_Pad1.08x0.95mm_HandSolder
D301: RCLAMP0582B; SOT-416
H201, H202, H203, H204: MountingHole; MountingHole_2.7mm_M2.5
IC201: MSP430FR2673; VQFN-32-1EP_5x5mm_P0.5mm_EP3.5x3.5mm
IC301: TXS0102DCU; VSSOP-8_2.3x2mm_P0.5mm
K301: SSM3K127TU; SOT-23
R202: 330; R_0603_1608Metric_Pad0.98x0.95mm_HandSolder
R203, R204: 10k NB; R_0603_1608Metric_Pad0.98x0.95mm_HandSolder
R301, R304: 10k n.b.; R_0603_1608Metric_Pad0.98x0.95mm_HandSolder
R302: 0R; R_0603_1608Metric_Pad0.98x0.95mm_HandSolder
R303: 0R n.b.; R_0603_1608Metric_Pad0.98x0.95mm_HandSolder
SW201: SKRKAEE020; SW_Push_SPST_NO_Alps_SKRK
SW202: A6H-8101; SW_DIP_SPSTx08_Slide_Omron_A6H-8101_W6.15mm_P1.27mm
X201: ESQ-104-14-G-D; PinSocket_2x04_P2.54mm_Vertical
X202: Conn_02x03_Counter_Clockwise; PinHeader_2x03_P2.54mm_Vertical
X203: Conn_01x03; PinHeader_1x03_P2.54mm_Vertical
X301: Molex Nano-Fit 103514-1*114; Molex_Nano-Fit_105314-xx14_2x07_P2.50mm_Horizontal
Y201: 9HT11-32.768KDZF-T; Crystal_SMD_TXC_9HT11-2Pin_2.0x1.2mm_HandSoldering
locked: 47k; R_0603_1608Metric_Pad0.98x0.95mm_HandSolder

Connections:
+3V3: C205.1, C206.1, C207.1, C301.1, IC201.32 (DVCC), IC301.3 (VCCA), R203.2, R204.2, R302.1, X201.1, X203.2, X301.2, locked.1
+5V: R303.1, X201.2, X301.9
+12V: X201.3, X301.8
/MCU/ADDR_B0: IC201.15 (P3.4/TA2CLK/COMP0OUT/CAP0.3), SW202.1
/MCU/ADDR_B1: IC201.14 (P2.3/TA2.0/CAP0.2), SW202.2
/MCU/ADDR_B2: IC201.13 (P3.3/TA2.1/CAP0.1), SW202.3
/MCU/ADDR_B3: IC201.12 (P3.0/TA2.2/CAP0.0), SW202.4
/MCU/ADDR_B4: IC201.11 (P2.2/SYNC/ACLK/COMP0.1), SW202.5
/MCU/GPIO_Reserve_B2B: IC201.8 (P1.1/UCB0CLK/TA0.1/COMP0.0/A1), X201.5
/MCU/Interface_Enable: IC201.26 (P3.5/UCB1CLK/TB0TRG/CAP3.1), IC301.6 (OE)
/MCU/Sensor_Lowside_Switch: IC201.25 (P2.7/UCB1STE/CAP3.0), K301.2
/MCU/TEST_SBWTCK: IC201.2 (TEST/SBWTCK), R202.2, X202.3
/MCU/UCB0_SCL: IC201.10 (P1.3/UCB0SOMI/UCB0SCL/MCLK/A3), R203.1, X201.7
/MCU/UCB0_SDA: IC201.9 (P1.2/UCB0SIMO/UCB0SDA/TA0.2/A2/Veref-), R204.1, X201.8
/MCU/UCB1_SCL: IC201.28 (P3.6/UCB1SOMI/UCB1SCL/CAP3.3), IC301.5 (A1)
/MCU/UCB1_SDA: IC201.27 (P3.2/UCB1SIMO/UCB1SDA/CAP3.2), IC301.4 (A2)
/MCU/VCC_TARGET: X202.6, X203.1
/MCU/VCC_TOOL: X202.5, X203.3
/MCU/XIN: C203.1, IC201.30 (P2.1/XIN), Y201.2
/MCU/XOUT: C204.1, IC201.29 (P2.0/XOUT), Y201.1
/MCU/~RST/SBWTDIO: C201.1, IC201.1 (~RST/NMI/SBWTDIO), SW201.2, X201.6, X202.1, locked.2
GND: C201.2, C202.2, C203.2, C204.2, C205.2, C206.2, C207.2, C301.2, D301.3 (A), IC201.31 (DVSS), IC201.33 (PAD), IC301.2 (GND), K301.3, SW201.1, SW202.12, SW202.13, SW202.14, SW202.15, SW202.16, X201.4, X202.4
unnamed: C202.1, IC201.20 (VREG)
unnamed: D301.1 (K1), IC301.8 (B1), R301.2, X301.4
unnamed: D301.2 (K2), IC301.1 (B2), R304.2, X301.11
unnamed: IC301.7 (VCCB), R301.1, R302.2, R303.2, R304.1
unnamed: R202.1, X202.2
unnamed: K301.1, X301.1

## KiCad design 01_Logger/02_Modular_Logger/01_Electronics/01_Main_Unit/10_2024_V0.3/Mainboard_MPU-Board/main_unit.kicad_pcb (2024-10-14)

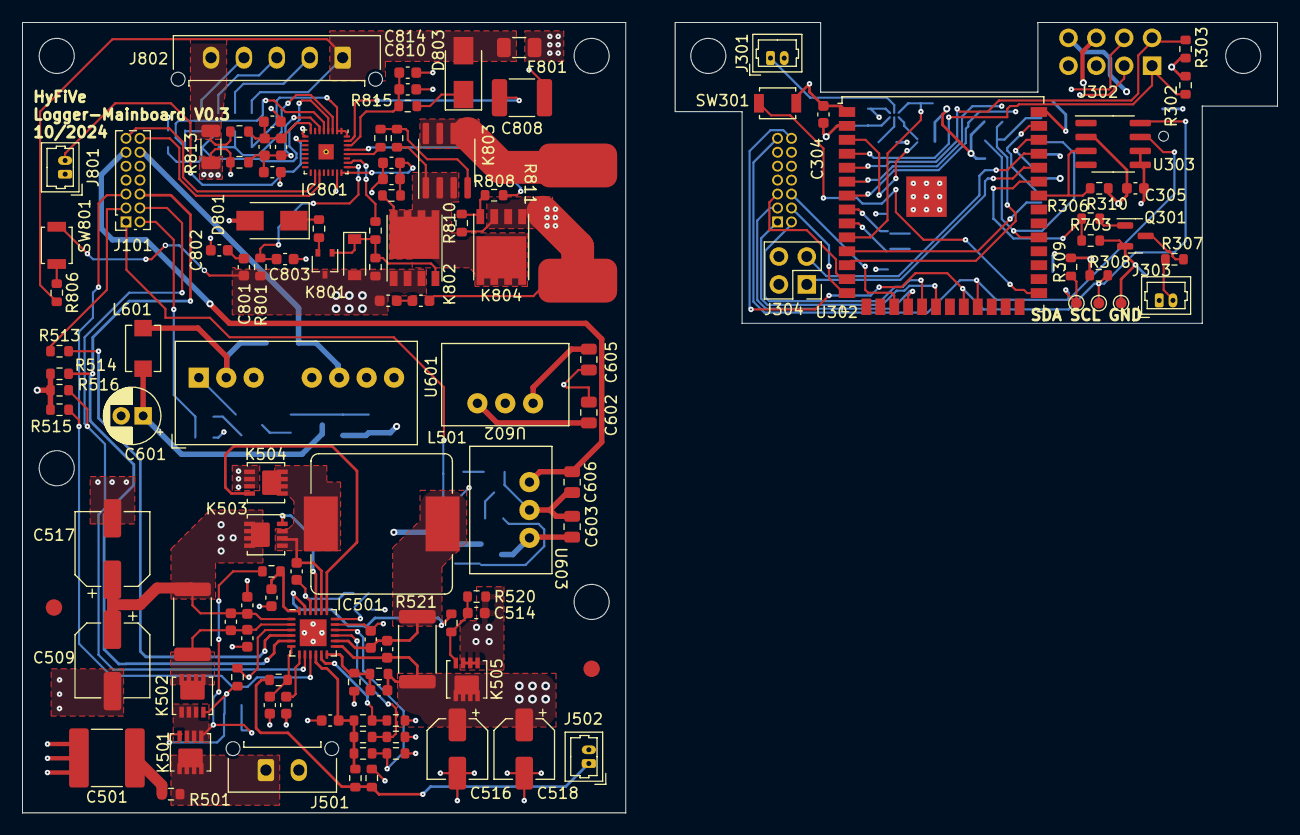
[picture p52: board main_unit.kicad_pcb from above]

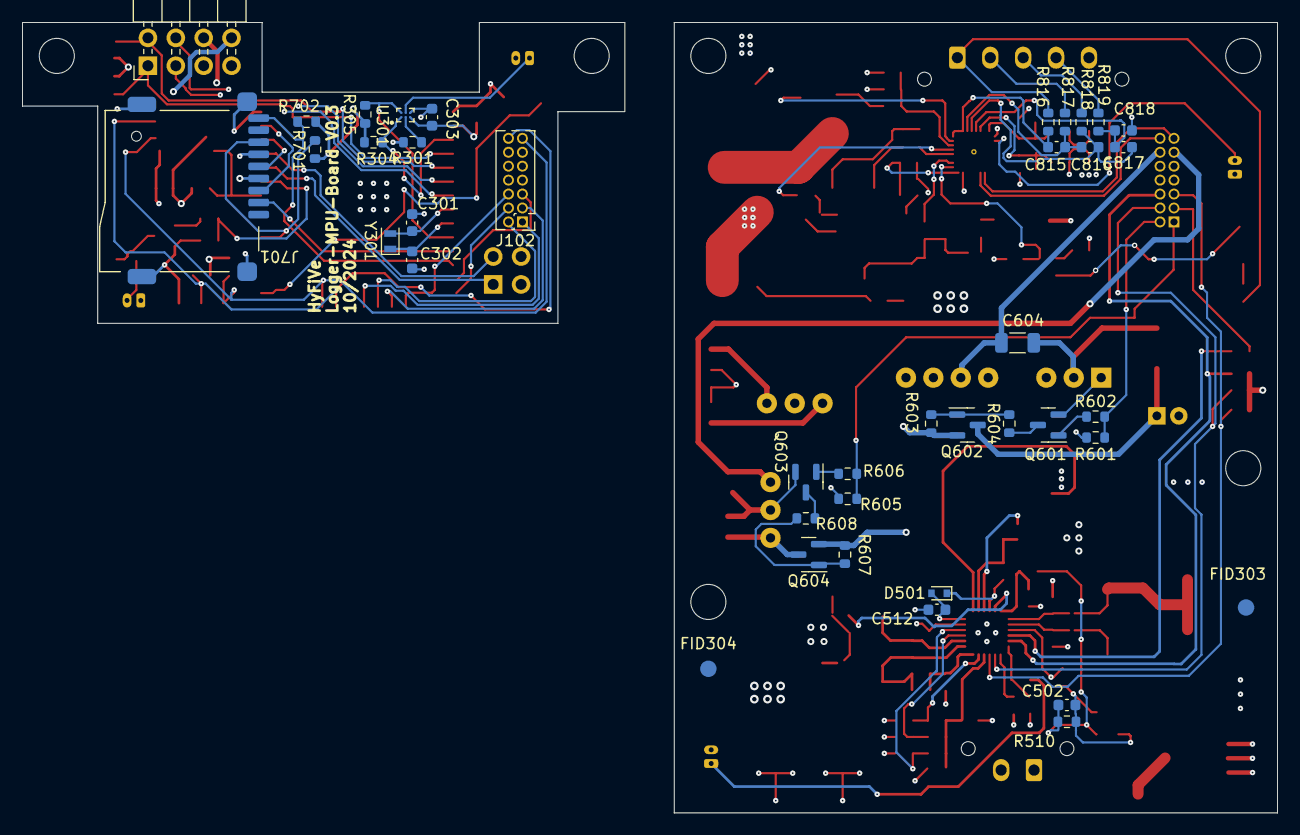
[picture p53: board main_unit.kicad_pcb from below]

Board: 4 copper layers, 114.4 x 72.1 mm, 167 parts (40 on the bottom side), 109 nets.

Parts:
C301, C302: 20pF; C_0603_1608Metric
C303, C304, C305, C502, C503, C505, C506, C507, C511, C513, C514, C515, C801, C802, C806, C807, C809, C812, C813, C815, C816, C817, C818: 100nF 50V; C_0603_1608Metric
C501: 47µF 35V X7R; C_2220_5650Metric
C504: 1µF 10V; C_0603_1608Metric
C508: 33nF 25V; C_0603_1608Metric
C509, C517: 47µF 35V; CP_Elec_6.3x5.4
C510, C512: 1µF 35V; C_0603_1608Metric
C516, C518: 20µF 35V; CP_Elec_5x5.3
C519: 22pF 35V; C_0603_1608Metric
C601: 10µF, 50V; CP_Radial_D5.0mm_P2.00mm
C602, C603: 22µF 30V; C_0805_2012Metric
C604: 150pF, 2kV; C_1206_3216Metric
C605, C606: 47µF 10V; C_0805_2012Metric
C803: 10nF, 50V; C_0603_1608Metric
C804, C805, C810, C814: 100pF 50V; C_0603_1608Metric
C808: 2,2µF 100V; C_1812_4532Metric
C811: 100pF 100V; C_0603_1608Metric
D501: BAT54W; D_SOD-523
D801, D803: SS1H10-E3/61T; D_SMA
D802: MMSZ5246B-7-F; D_SOD-123
F801: 12A; Fuse_1206_3216Metric
FID301, FID302, FID303, FID304: Fiducial; Passmarke
H301, H302, H303, H304, H305, H306: MountingHole; MountingHole_3.2mm_M3_ISO7380
IC501: BQ24618; VQFN-24-1EP_4x4mm_P0.5mm_EP2.45x2.45mm
IC801: BQ40Z80; RSM32 VQFN-32-1EP_4x4mm_P0.4mm_EP1.4x1.4mm_ThermalVias
J101: SFMC-107-01-L-D; PinSocket_2x07_P1.27mm_Vertical
J102: FTS-107-01-F-D; PinHeader_2x07_P1.27mm_Vertical
J301, J303: Conn_01x02; Molex_PicoBlade_53047-0210_1x02_P1.25mm_Vertical
J302: Conn_02x04_Counter_Clockwise; PinHeader_2x04_P2.54mm_Horizontal
J304: Conn_02x02_Odd_Even; PinHeader_2x02_P2.54mm_Vertical
J501: Conn_01x02; Molex_Micro-Fit_3.0_43650-0215_1x02_P3.00mm_Vertical
J502: Conn_01x02_Female; Molex_PicoBlade_53047-0210_1x02_P1.25mm_Vertical
J701: Micro_SD_Card_Det; SD_CARD_693071020811
J801: Conn_01x02_Male; Molex_PicoBlade_53047-0210_1x02_P1.25mm_Vertical
J802: Conn_01x05_Male; Molex_Micro-Fit_3.0_43650-0515_1x05_P3.00mm_Vertical
K501, K502, K505: SISH101DN-T1-GE3; PowerPAK 1212-8 Single
K503, K504: SiS412DN; PowerPAK 1212-8 Single
K801: 2N7002KW; SOT-323_SC-70
K802, K804: CSD18540Q5B; TI Q5B-Package
K803: DMP6023LSS-13; SOIC-8_3.9x4.9mm_P1.27mm
L501: 3,3µH; L_Bourns_SRP1245A
L601: 10µH; CC453232A
Q301: BSS138; SOT-23
Q601, Q603: BSS123; SOT-23
Q602, Q604: IRLML5203TRPBF; SOT-23
R301, R506, R509, R510, R520: 100k; R_0603_1608Metric
R302, R303, R304, R305, R308, R309, R310, R502, R507, R701, R702, R802, R809: 10k; R_0603_1608Metric
R306, R602, R606: 47k; R_0603_1608Metric
R307: 75; R_0603_1608Metric
R501, R511, R812, R814, R815: 100; R_0603_1608Metric
R503: 5.7k; R_0603_1608Metric
R504: R_Therm_1; R_0603_1608Metric
R505: R_Therm_2; R_0603_1608Metric
R508: 232k; R_0603_1608Metric
R512, R519, R604, R608, R808: 1k; R_0603_1608Metric
R513: 0; R_0603_1608Metric
R514, R515, R516, R523: 49,9k; R_0603_1608Metric
R517, R521: 10m; R_2512_6332Metric
R518: 10; R_0603_1608Metric
R522: 357k; R_0603_1608Metric
R601, R605: 2k7; R_0603_1608Metric
R603, R607: 680k; R_0603_1608Metric
R703: 1M; R_0603_1608Metric
R801: 1,1k; R_0603_1608Metric
R803, R807, R810: 10M; R_0603_1608Metric
R804: 4,81k; R_0603_1608Metric
R805: 510; R_0603_1608Metric
R806: 51; R_0603_1608Metric
R811: 46.4 5W; R_4527_11570Metric
R813: 1m; R_1206_3216Metric
R816, R817, R818, R819: 499; R_0603_1608Metric
SW301, SW801: SW_Push; SW_SPST_B3U-1000P
TP301, TP302, TP303: TestPoint; TestPoint_Pad_D1.0mm
U301: MAX16125WTEG00+T; WLP-6
U302: ESP32-S3-WROOM-1U
U303: DS3231MZ; SOIC-8_3.9x4.9mm_P1.27mm
U601: SPBW06F-12; Converter_DCDC_XP_POWER-ITxxxxxS_THT
U602: OKI-78SR-3.3_1.5-W36-C; DC_DC_Converter
U603: OKI-78SR-5_1.5-W36-C; DC_DC_Converter
Y301: Crystal; Crystal_SMD_TXC_9HT11-2Pin_2.0x1.2mm

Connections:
+3V3: C303.1, C304.1, C305.1, C605.1, J101.10, J102.10, J302.8, J303.1, J304.2, J701.4 (VDD), R302.1, R303.1, R304.1, R305.1, R308.1, R309.1, R310.1, R514.1, R515.1, R516.1, R701.2, R702.1, U301.C1 (VCC), U302.2 (VDD), U303.2 (VCC), U602.3 (OUT)
+5V: C606.1, J101.11, J102.11, J302.7, U603.3 (OUT)
+12V: C604.2, J101.12, J102.12, J302.6, U601.6 (+VOUT)
/MPU/Charge_Enable: J102.3, U302.18 (IO10)
/MPU/ENABLE_5V: J102.1, U302.20 (IO12)
/MPU/ENABLE_12V: J102.2, U302.19 (IO11)
/MPU/GPIO_Reserve_B2B: J302.4, U302.6 (IO6)
/MPU/I2C_BUS_CLK: J302.2, R303.2, U302.5 (IO5)
/MPU/I2C_BUS_SDA: J302.1, R302.2, U302.4 (IO4)
/MPU/I2C_SMBus_SCL: J102.14, R308.2, TP301.1, U302.22 (IO14), U303.8 (SCL)
/MPU/I2C_SMBus_SDA: J102.13, R309.2, TP302.1, U302.23 (IO21), U303.7 (SDA)
/MPU/Interface_RST: J302.3, U302.7 (IO7)
/MPU/LED_STATUS: R306.1, R703.1, U302.35 (IO42)
/MPU/RST: R304.2, U301.A1 (/RESET), U302.3 (EN)
/MPU/RTC_INTERRUPT: R310.2, U302.34 (IO41), U303.3 (~INT/SQW)
/MPU/SD_CARD_DETECT: J701.9 (DET_B), R702.2, U302.12 (IO8)
/MPU/SD_V_SPI_CLK: J701.5 (CLK), U302.38 (IO2)
/MPU/SD_V_SPI_CS: J701.2 (DAT3/CD), U302.11 (IO18)
/MPU/SD_V_SPI_MISO: J701.7 (DAT0), R701.1, U302.31 (IO38)
/MPU/SD_V_SPI_MOSI: J701.3 (CMD), U302.39 (IO1)
/MPU/UART_RXD0: J304.1, U302.36 (RXD0)
/MPU/UART_TXD0: J304.3, U302.37 (TXD0)
/MPU/~PG: J102.4, U302.14 (IO20)
/MPU/~STAT1: J102.6, U302.17 (IO9)
/MPU/~STAT2: J102.5, U302.13 (IO19)
/power/BMS/BAT_MINUS: J802.5, R813.2, R814.1
/power/BMS/BAT_PLUS: D803.2 (A), F801.2, J802.1, R806.2, R816.1
/power/BMS/BAT_PLUS_F: C807.1, F801.1, K804.1, K804.2, K804.3, R810.2, R811.2
/power/BMS/PACK+: C515.1, C516.1, C518.1, C519.2, C801.1, C806.1, D802.2 (A), IC501.13 (SRN), K505.5, K505.6, K505.7, K505.8, K505.9, K801.3, K802.1, K802.2, K802.3, R521.1, R522.1, R801.2, R803.2, SW801.2
/power/Battery_Charger/ACP: C503.2, C505.1, IC501.2 (ACP), K502.5, K502.6, K502.7, K502.8, K502.9, R517.2
/power/Battery_Charger/Thermistor: J502.1, R504.1, R505.2, R511.1
/power/Battery_Charger/VIN: J501.1, K501.5, K501.6, K501.7, K501.8, K501.9, R501.1
/power/Battery_Charger/VREF: C504.1, IC501.10 (VREF), R502.1, R504.2, R506.1, R508.1
/power/Charge_Enable: J101.3, R513.1
/power/ENABLE_5V: J101.1, R605.2, R606.1
/power/ENABLE_12V: J101.2, R601.2, R602.1
/power/I2C_SMBus_SCL: IC801.19 (SMBC), J101.14
/power/I2C_SMBus_SDA: IC801.18 (SMBD), J101.13
/power/System+: C505.2, C507.2, C509.1, C514.1, C517.1, C602.1, IC501.1 (ACN), K503.5, K503.6, K503.7, K503.8, K503.9, K505.1, K505.2 (S), K505.3 (S), Q602.2 (S), Q604.2 (S), R517.1, R520.1, R603.2, R607.2, U602.1 (IN)
/power/~PG: IC501.8 (~PG), J101.4, R516.2
/power/~STAT1: IC501.5 (~STAT1), J101.6, R514.2
/power/~STAT2: IC501.9 (~STAT2), J101.5, R515.2
GND: C301.2, C302.2, C303.2, C304.2, C305.2, C501.2, C503.1, C504.2, C506.1, C507.1, C508.1, C509.2, C510.2, C512.2, C513.1, C516.2, C517.2, C518.2, C601.2, C602.2, C603.2, C605.2, C606.2, C802.2, C803.2, C804.1, C805.1, C808.2, C809.1, C810.1, C813.1, C814.1, C818.2, D801.2 (A), IC501.17 (GND), IC501.25 (PwrPad), IC801.9 (VSS), IC801.23 (FUSE), IC801.33 (PAD), J101.7, J101.8, J102.7, J102.8, J301.2, J302.5, J304.4, J501.2, J502.2, J701.6 (VSS), J701.10 (DET_A), J701.11 (SHIELD), J701.12 (SHIELD), J701.13 (SHIELD), J801.1, K504.1, K504.2 (S), K504.3 (S), Q301.2 (S), Q601.2 (S), Q603.2 (S), R301.2, R503.2, R505.1, R507.2, R509.2, R523.2, R601.1, R605.1, R703.2, R812.2, R813.1, SW301.2, TP303.1, U301.C2 (GND), U302.1 (GND), U302.40 (GND), U302.EPAD (GND), U303.5 (GND), U303.6 (VBAT), U601.1 (-VIN), U601.7 (-VOUT), U602.2 (GND), U603.2 (GND)
unnamed: C501.1, R501.2
unnamed: C502.1, K501.1, K501.2 (S), K501.3 (S), K502.1, K502.2 (S), K502.3 (S), R510.1, R518.2
unnamed: C502.2, K501.4, K502.4, R510.2, R512.1
unnamed: C514.2, K505.4, R519.1, R520.2
unnamed: C801.2, C802.1
unnamed: C806.2, C807.2
unnamed: C512.1, D501.2 (A), IC501.18 (REGN)
unnamed: C511.1, D501.1 (K), IC501.22 (BTST)
unnamed: D801.1 (K), R802.1
unnamed: D802.1 (K), K801.1, K802.4, R803.1, R804.2
unnamed: D803.1 (K), R815.1
unnamed: IC501.16 (ACSET), R502.2, R503.1
unnamed: IC501.4 (CE), R513.2
unnamed: IC501.21 (HIDRV), K503.4
unnamed: IC501.11 (ISET1), R508.2, R509.1
unnamed: IC501.15 (ISET2), R506.2, R507.1
unnamed: IC501.19 (LODRV), K504.4
unnamed: C511.2, IC501.20 (PH), K503.1, K503.2 (S), K503.3 (S), K504.5, K504.6, K504.7, K504.8, K504.9, L501.1
unnamed: C513.2, C515.2, IC501.14 (SRP), L501.2, R521.2
unnamed: C506.2, IC501.6 (TS), R511.2
unnamed: C508.2, IC501.7 (TTC)
unnamed: C510.1, IC501.24 (VCC), R518.1
unnamed: C519.1, IC501.12 (VFB), R522.2, R523.1
unnamed: IC501.3 (~ACDRV), R512.2
unnamed: IC501.23 (~BATDRV), R519.2
unnamed: C810.2, C814.2, IC801.30 (BAT), R815.2
unnamed: IC801.29 (CHG), R808.1
unnamed: IC801.26 (DSG), R804.1
unnamed: C808.1, IC801.31 (PBI)
unnamed: IC801.28 (PCHG), R809.1
unnamed: C803.1, IC801.25 (Pack), R801.1
unnamed: C809.2, C811.2, C812.2, IC801.6 (SRN), R812.1
unnamed: C811.1, C812.1, C813.2, IC801.8 (SRP), R814.2
unnamed: IC801.10 (TS1), J801.2
unnamed: C817.2, C818.1, IC801.5 (VC1), R819.2
unnamed: C816.2, C817.1, IC801.4 (VC2), R818.2
unnamed: C815.2, C816.1, IC801.3 (VC3), R817.2
unnamed: C815.1, IC801.1 (VC5), IC801.2 (VC4), IC801.32 (VC6), R816.2
unnamed: C804.2, C805.2, IC801.24 (VCC), R805.1
unnamed: J301.1, U301.B2 (/MR)
unnamed: J303.2, R307.1
unnamed: J802.2, R817.1
unnamed: J802.3, R818.1
unnamed: J802.4, R819.1
unnamed: K801.2, R802.2
unnamed: K802.5, K802.6, K802.7, K802.8, K802.9, K803.1, K803.2, K803.3, K804.5, K804.6, K804.7, K804.8, K804.9, R805.2, R807.2
unnamed: K803.4, R807.1, R809.2
unnamed: K803.5, K803.6, K803.7, K803.8, R811.1
unnamed: K804.4, R808.2, R810.1
unnamed: Q301.3 (D), R307.2
unnamed: Q301.1 (G), R306.2
unnamed: Q601.3 (D), R604.1
unnamed: Q601.1 (G), R602.2
unnamed: C601.1, L601.1, Q602.3 (D)
unnamed: Q602.1 (G), R603.1, R604.2
unnamed: Q603.3 (D), R608.1
unnamed: Q603.1 (G), R606.2
unnamed: C603.1, Q604.3 (D), U603.1 (IN)
unnamed: Q604.1 (G), R607.1, R608.2
unnamed: R806.1, SW801.1
unnamed: R301.1, U301.B1 (SEL)
unnamed: R305.2, U301.A2 (/SRESET), U302.10 (IO17)
unnamed: SW301.1, U302.27 (IO0)
unnamed: C301.1, U302.8 (IO15), Y301.2
unnamed: C302.1, U302.9 (IO16), Y301.1
unnamed: C604.1, L601.2, U601.2 (+VIN)

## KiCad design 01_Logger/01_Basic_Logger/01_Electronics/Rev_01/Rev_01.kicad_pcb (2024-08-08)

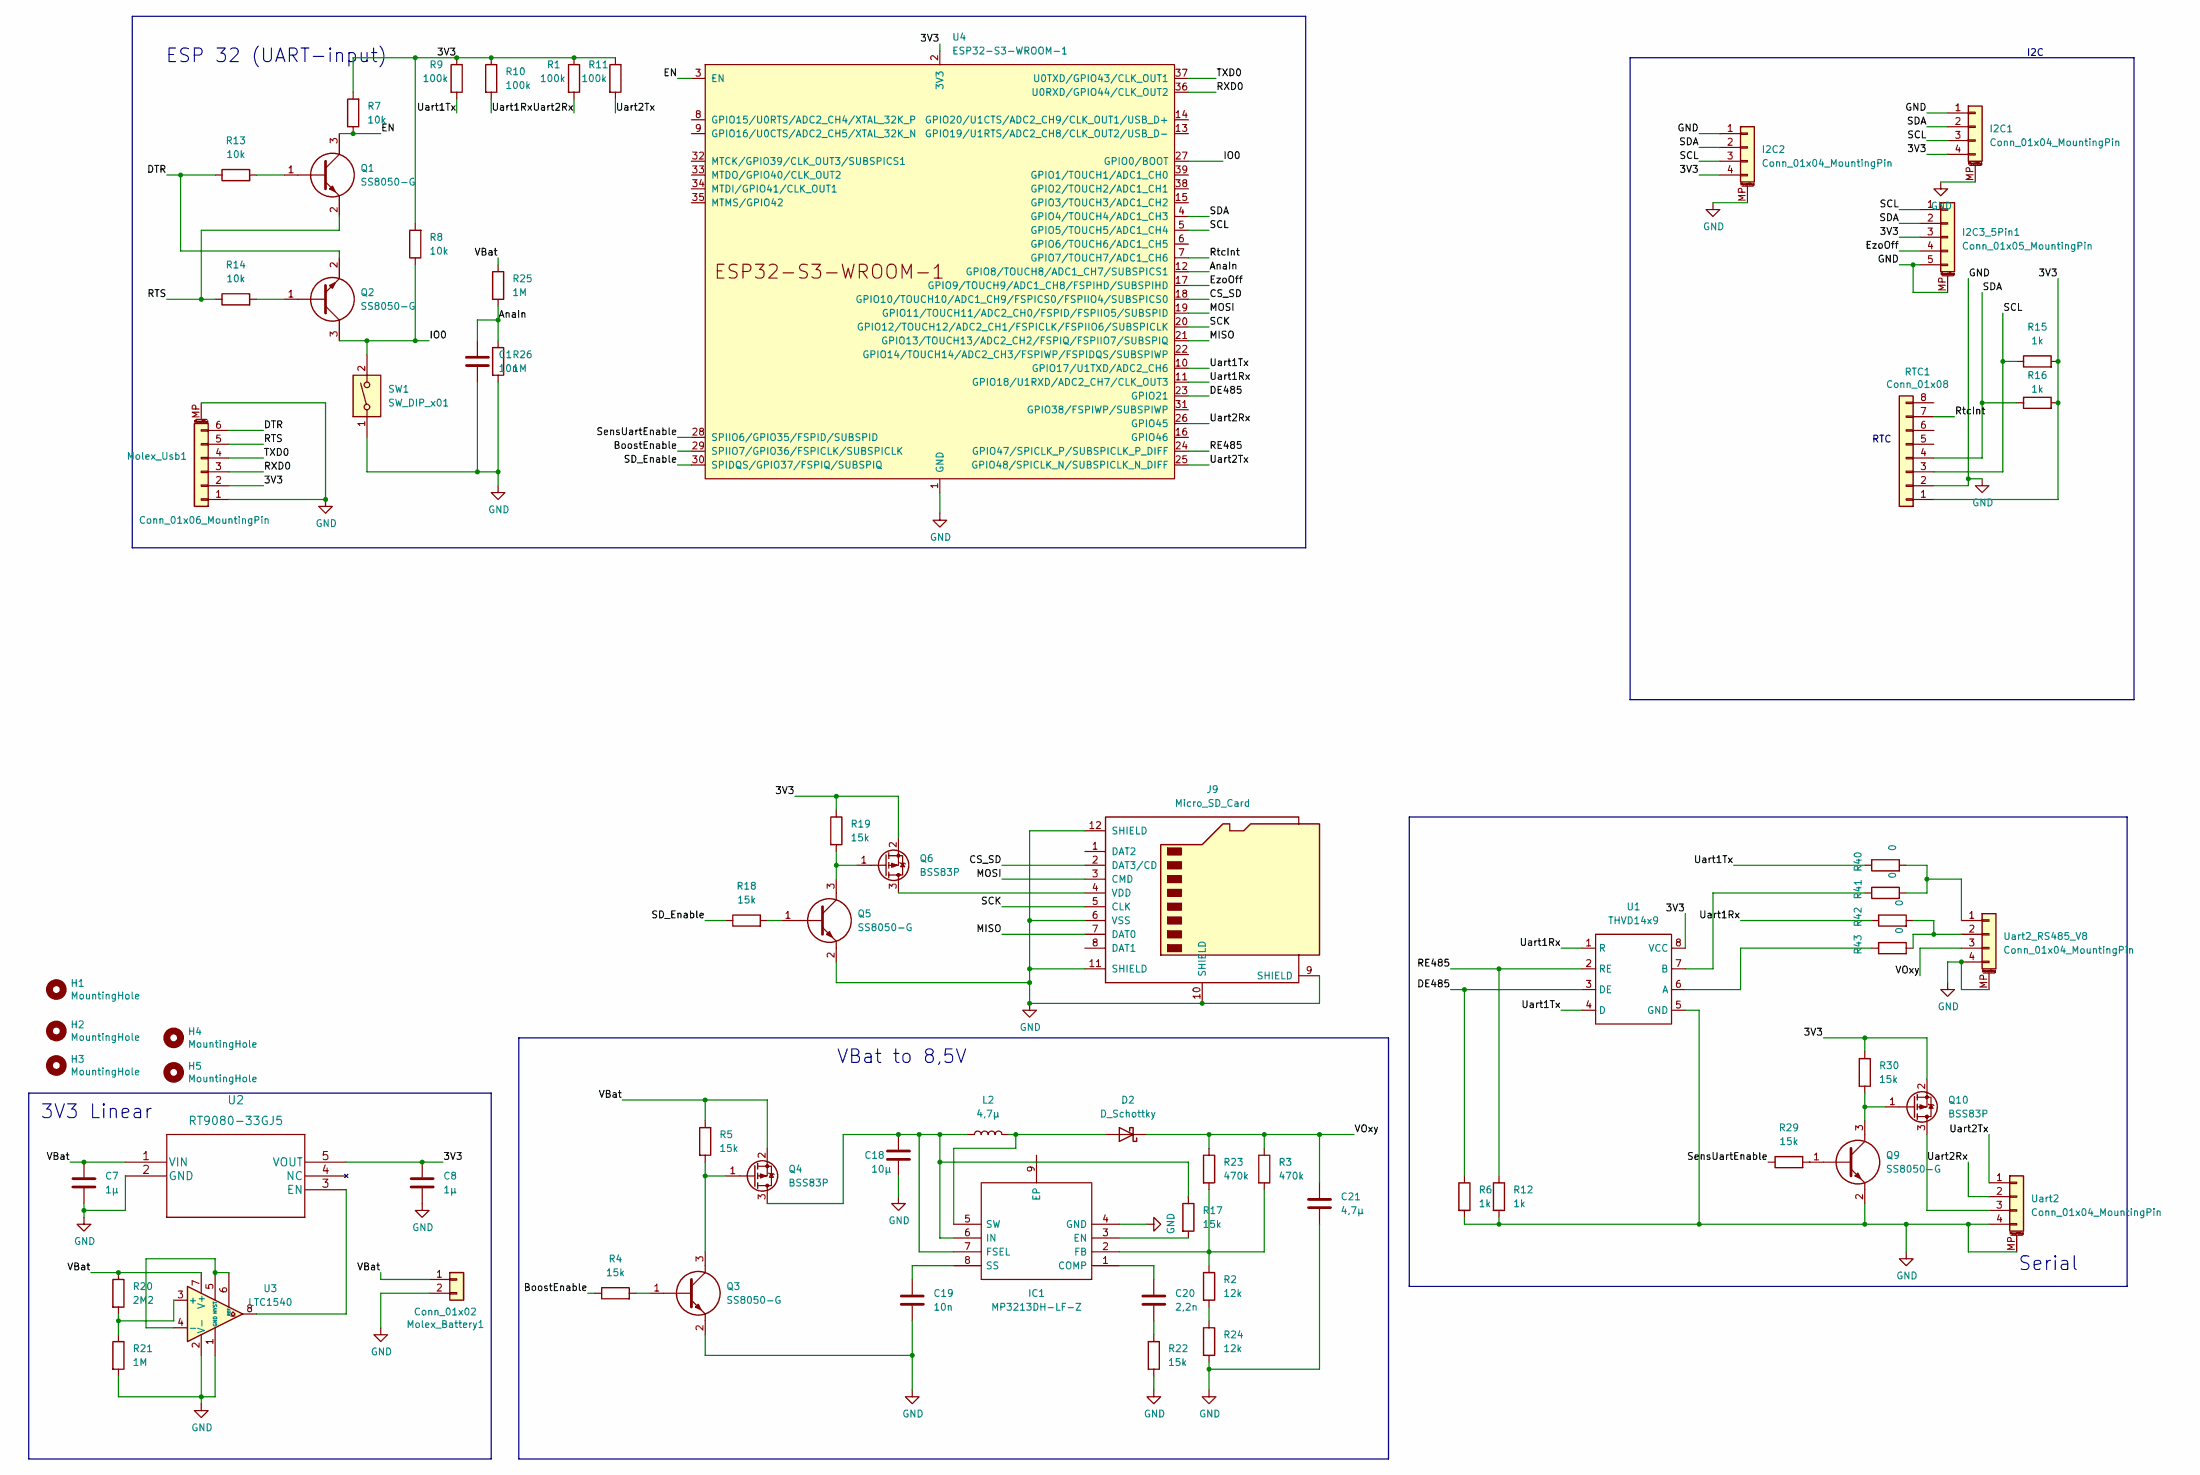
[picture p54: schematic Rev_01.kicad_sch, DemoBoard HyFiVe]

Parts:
C1, C19: 10n; C_0805_2012Metric
C7, C8: 1µ; C_0805_2012Metric
C18: 10µ; C_0805_2012Metric; Manufacturer_Part_Number TMK212BBJ106KG8T
C20: 2,2n; C_0805_2012Metric
C21: 4,7µ; C_0805_2012Metric; Manufacturer_Part_Number GCM21BC71E475KE36L
D2: D_Schottky; D_1206_3216Metric; Manufacturer_Part_Number CD1206-B240
H1, H2, H3: MountingHole; MountingHole_3.2mm_M3
H4, H5: MountingHole; MountingHole_3.2mm_M3_DIN965
I2C1, I2C2: Conn_01x04_MountingPin; Molex_PicoBlade_53261-0471_1x04-1MP_P1.25mm_Horizontal; Manufacturer_Part_Number 53261-0471
I2C3_5Pin1: Conn_01x05_MountingPin; Molex_PicoBlade_53261-0571_1x05-1MP_P1.25mm_Horizontal; Manufacturer_Part_Number 53261-0571
IC1: MP3213DH-LF-Z; MSOP-8-1EP_3x3mm_P0.65mm_EP1.95x2.15mm; Mouser Part Number 946-MP3213DHLFZ
J9: Micro_SD_Card; GCT_MEM2067-02-180-00-A_REVB; Manufacturer_Part_Number MEM2067-02-180-00-A
L2: 4,7µ; L_Bourns-SRN4018; Manufacturer_Part_Number SRN4018-4R7M
Molex_Battery1: Conn_01x02; Molex_MicroClasp_55935-0230_1x02_P2.00mm_Horizontal; Manufacturer_Part_Number 55935-0230
Molex_Usb1: Conn_01x06_MountingPin; Molex_PicoBlade_53261-0671_1x06-1MP_P1.25mm_Horizontal; Manufacturer_Part_Number 53261-0671
Q1, Q2, Q3, Q5, Q9: SS8050-G; SOT-23-3; Mouser Part Number 750-SS8050-G
Q4, Q6, Q10: BSS83P; SOT-23; Manufacturer_Part_Number MMFTP84
R1, R9, R10, R11: 100k; R_0603_1608Metric
R2, R24: 12k; R_0603_1608Metric
R3, R23: 470k; R_0603_1608Metric
R4, R5, R17, R18, R19, R22, R29, R30: 15k; R_0603_1608Metric
R6, R12, R15, R16: 1k; R_0603_1608Metric
R7, R8, R13, R14: 10k; R_0603_1608Metric
R20: 2M2; R_0603_1608Metric
R21, R25, R26: 1M; R_0603_1608Metric
R40, R41, R42, R43: 0; R_0603_1608Metric
RTC1: Conn_01x08; DS3231Module; Manufacturer_Part_Number 3013
SW1: SW_DIP_x01; SW_DIP_SPSTx01_Slide_6.7x4.1mm_W8.61mm_P2.54mm_LowProfile; Manufacturer_Part_Number 434111025826
U1: THVD14x9; SOIC-8_3.9x4.9mm_P1.27mm; Manufacturer_Part_Number THVD1429DT
U2: RT9080-33GJ5; SOT-23-5; Manufacturer_Part_Number RT9080-33GJ5
U3: LTC1540; SOIC-8-1EP_3.9x4.9mm_P1.27mm_EP2.29x3mm; Manufacturer_Part_Number LTC1540CS8#TRPBF
U4: ESP32-S3-WROOM-1; ESP32-S3-WROOM-1U; Manufacturer_Part_Number ESP32-S3-WROOM-1U-N16R2
Uart2, Uart2_RS485_V8: Conn_01x04_MountingPin; Molex_PicoBlade_53261-0471_1x04-1MP_P1.25mm_Horizontal; Manufacturer_Part_Number 53261-0471

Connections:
/3V3: C8.1, I2C1.4, I2C2.4, I2C3_5Pin1.3, Molex_Usb1.2, Q6.2 (S), Q10.2 (S), R1.1, R7.2, R8.2, R9.1, R10.1, R11.1, R15.2, R16.2, R19.1, R30.1, RTC1.1, U1.8 (VCC), U2.5 (VOUT), U4.2 (3V3)
/AnaIn: C1.1, R25.2, R26.1, U4.12 (GPIO8/TOUCH8/ADC1_CH7/SUBSPICS1)
/BoostEnable: R4.1, U4.29 (SPIIO7/GPIO36/FSPICLK/SUBSPICLK)
/CS_SD: J9.2 (DAT3/CD), U4.18 (GPIO10/TOUCH10/ADC1_CH9/FSPICS0/FSPIIO4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)
/DE485: R6.1, U1.3 (DE), U4.23 (GPIO21)
/DTR: Molex_Usb1.6, Q2.2, R13.1
/EN: Q1.3, R7.1, U4.3 (EN)
/EzoOff: I2C3_5Pin1.4, U4.17 (GPIO9/TOUCH9/ADC1_CH8/FSPIHD/SUBSPIHD)
/IO0: Q2.3, R8.1, SW1.2, U4.27 (GPIO0/BOOT)
/MISO: J9.7 (DAT0), U4.21 (GPIO13/TOUCH13/ADC2_CH2/FSPIQ/FSPIIO7/S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)
/MOSI: J9.3 (CMD), U4.19 (GPIO11/TOUCH11/ADC2_CH0/FSPID/FSPIIO5/S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)
/RE485: R12.1, U1.2 (RE), U4.24 (GPIO47/SPICLK_P/SUBSPICLK_P_DIFF)
/RTS: Molex_Usb1.5, Q1.2, R14.1
/RXD0: Molex_Usb1.3, U4.36 (U0RXD/GPIO44/CLK_OUT2)
/RtcInt: RTC1.7, U4.7 (GPIO7/TOUCH7/ADC1_CH6)
/SCK: J9.5 (CLK), U4.20 (GPIO12/TOUCH12/ADC2_CH1/FSPICLK/FSPIIO6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)
/SCL: I2C1.3, I2C2.3, I2C3_5Pin1.1, R15.1, RTC1.3, U4.5 (GPIO5/TOUCH5/ADC1_CH4)
/SDA: I2C1.2, I2C2.2, I2C3_5Pin1.2, R16.1, RTC1.4, U4.4 (GPIO4/TOUCH4/ADC1_CH3)
/SD_Enable: R18.1, U4.30 (SPIDQS/GPIO37/FSPIQ/SUBSPIQ)
/SensUartEnable: R29.1, U4.28 (SPIIO6/GPIO35/FSPID/SUBSPID)
/TXD0: Molex_Usb1.4, U4.37 (U0TXD/GPIO43/CLK_OUT1)
/Uart1Rx: R10.2, R42.1, U1.1 (R), U4.11 (GPIO18/U1RXD/ADC2_CH7/CLK_OUT3)
/Uart1Tx: R9.2, R40.1, U1.4 (D), U4.10 (GPIO17/U1TXD/ADC2_CH6)
/Uart2Rx: R1.2, U4.26 (GPIO45), Uart2.2
/Uart2Tx: R11.2, U4.25 (GPIO48/SPICLK_N/SUBSPICLK_N_DIFF), Uart2.1
/VBat: C7.1, Molex_Battery1.1, Q4.2 (S), R5.1, R20.1, R25.1, U2.1 (VIN), U3.7 (V+)
/VOxy: C21.1, D2.1 (K), R3.1, R23.1, Uart2_RS485_V8.3
GND: C1.2, C7.2, C8.2, C18.2, C19.2, C21.2, I2C1.1, I2C1.MP (MountPin), I2C2.1, I2C2.MP (MountPin), I2C3_5Pin1.5, I2C3_5Pin1.MP (MountPin), IC1.4 (GND), J9.6 (VSS), J9.9 (SHIELD), J9.10 (SHIELD), J9.11 (SHIELD), J9.12 (SHIELD), Molex_Battery1.2, Molex_Usb1.1, Molex_Usb1.MP (MountPin), Q3.2, Q5.2, Q9.2, R6.2, R12.2, R21.2, R22.2, R24.2, R26.2, RTC1.2, SW1.1, U1.5 (GND), U2.2 (GND), U3.1 (GND), U3.2 (V-), U4.1 (GND), U4.40 (GND), U4.41 (GND), Uart2.4, Uart2.MP (MountPin), Uart2_RS485_V8.4, Uart2_RS485_V8.MP (MountPin)
unnamed: C20.2, R22.1
unnamed: D2.2 (A), IC1.5 (SW), L2.2
unnamed: C20.1, IC1.1 (COMP)
unnamed: IC1.3 (EN), R17.2
unnamed: IC1.2 (FB), R2.1, R3.2, R23.2
unnamed: C18.1, IC1.6 (IN), IC1.7 (FSEL), L2.1, Q4.3 (D), R17.1
unnamed: C19.1, IC1.8 (SS)
unnamed: J9.4 (VDD), Q6.3 (D)
unnamed: Q1.1, R13.2
unnamed: Q2.1, R14.2
unnamed: Q3.1, R4.2
unnamed: Q3.3, Q4.1 (G), R5.2
unnamed: Q5.1, R18.2
unnamed: Q5.3, Q6.1 (G), R19.2
unnamed: Q9.1, R29.2
unnamed: Q10.3 (D), Uart2.3
unnamed: Q9.3, Q10.1 (G), R30.2
unnamed: R2.2, R24.1
unnamed: R43.1, U1.6 (A)
unnamed: R41.1, U1.7 (B)
unnamed: U2.3 (EN), U3.8
unnamed: R20.2, R21.1, U3.3 (+)
unnamed: U3.4 (-), U3.5 (HYST), U3.6 (REF)
unnamed: R40.2, R41.2, Uart2_RS485_V8.1
unnamed: R42.2, R43.2, Uart2_RS485_V8.2

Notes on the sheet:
ESP 32 (UART-input)
VBat to 8,5V
3V3 Linear
Serial
RTC
I2C

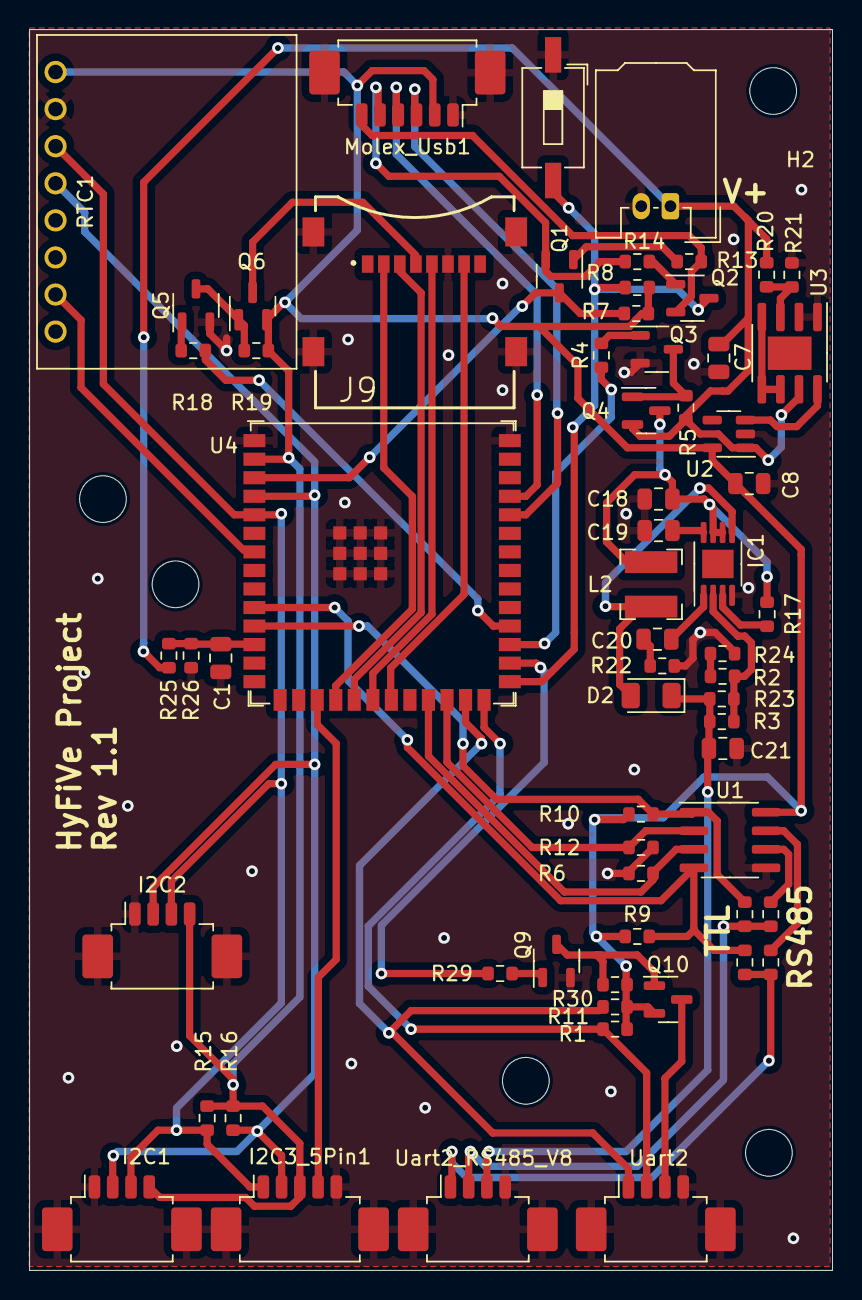
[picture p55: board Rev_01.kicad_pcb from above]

Board: 2 copper layers, 55.0 x 85.0 mm, 69 parts (0 on the bottom side), 53 nets.

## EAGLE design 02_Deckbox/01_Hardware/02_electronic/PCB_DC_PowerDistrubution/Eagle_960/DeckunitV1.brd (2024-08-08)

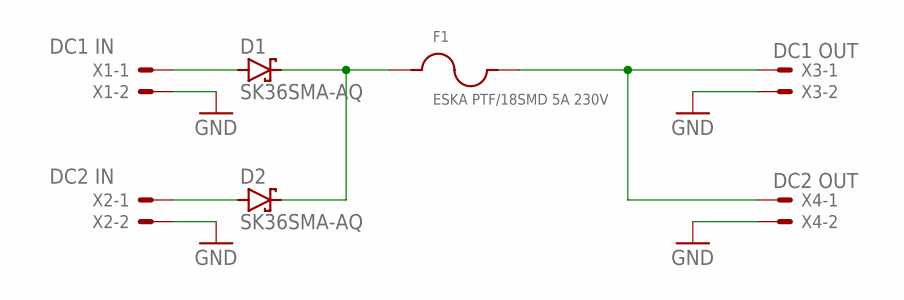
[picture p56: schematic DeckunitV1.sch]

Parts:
D1, D2: SK36SMA-AQ; SMA
F1: ESKA PTF/18SMD 5A 230V; 65800001109
X1: DC1 IN; 2PIN
X2: DC2 IN; 2PIN
X3: DC1 OUT; 2PIN
X4: DC2 OUT; 2PIN

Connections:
GND: X1.2, X2.2, X3.2, X4.2
V1+: D1.A, X1.1
V2+: D2.A, X2.1
V+: D1.C, D2.C, F1.1
V+F: F1.2, X3.1, X4.1

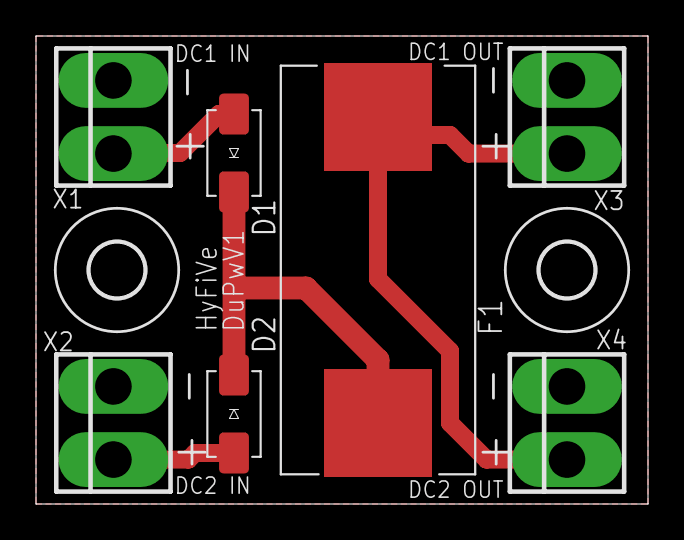
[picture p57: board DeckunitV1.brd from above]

Board: 2 copper layers, 34.0 x 26.0 mm, 9 parts (0 on the bottom side), 5 nets.

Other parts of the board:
U$1, U$2: 3,0

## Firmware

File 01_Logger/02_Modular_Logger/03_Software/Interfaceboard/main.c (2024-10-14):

/*
 * CopyrightText: (C) 2024 Hensel Elektronik GmbH
 *
 * License-Identifier: MPL-2.0
 *
 * Project: Hydrography on Fishing Vessels
 * Project URL: <https://github.com/HyFiVeUser/HyFiVe>, <https://hyfive.info>
 *
 * Description: main loop, callback functions for i2c slave interface
 */

#include <I2Cslave/i2c_slave.h>
#include <msp430.h>
#include <stdbool.h>
#include <stdint.h>
#include <stdio.h>
#include "driver/Csensori2c.h"
#include "driver/bluerobo/CMS5837.h"
#include "driver/bluerobo/CTSYS01.h"
#include "driver/Analog/Analog.h"
#include "driver/AtlasEZO/AtlasEZO.h"
#include "driver/KellerPressure/KellerPressure.h"
#include "driver/pyro/pyroPicoO2.h"
#include "sensor_config.h"

#define MCLK_FREQ_MHZ 8                     // MCLK = 8MHz
unsigned char getOwnI2CAddress(void);
void setPins(void);

/* callback for start condition */
void start_cb();

/* callback for bytes received */
void receive_cb(unsigned char receive);

/* callback to transmit bytes */
void transmit_cb(unsigned char volatile *byte);

/* last command */
volatile uint8_t cmd = CMD_UNKNOWN;

/* last parameter */
volatile uint8_t par[5] = {PAR_UNKNOWN, PAR_UNKNOWN, PAR_UNKNOWN, PAR_UNKNOWN, PAR_UNKNOWN};

/* response to send out on read req. */
volatile uint8_t res[8] = {RES_ERROR, RES_ERROR, RES_ERROR, RES_ERROR, RES_ERROR, RES_ERROR, RES_ERROR, RES_ERROR};

volatile uint8_t  byteCount      = 0;
uint8_t FW_VERSION = 0;
uint32_t version = 0x0;
uint8_t parameter = 0xFF;
volatile int64_t values[2]      = {0, 0};
volatile int64_t rawValues[2]      = {0, 0};
volatile uint8_t startConversion    = 1; //used as command flag and readyflag and errorflag
                                //0: conversion in progress
                                //1: nothing happening / ready
                                //2: fault in conversion
volatile int32_t  lastTemperature = -2999; //last Temperature in centigrad
volatile bool    setTemperature   = false;
volatile bool    setCalib   = false;
volatile bool calibrated = false;
volatile bool goToSleep = false;
volatile bool wakeUp = false;
volatile bool sleepOrWarmup = false;
volatile uint8_t calibToSet = 0;
volatile float   floatToSet = 0.0;

// Sensor WakeUp Time
uint16_t sensorWakeUpTime = 0;

void process_cmd(unsigned char cmd, unsigned char* par0)
{
    res[0] = RES_ERROR;

    union {
        float float_variable;
        unsigned char temp_array[4];
      } u;

    switch(cmd) {
    case CMD_PING:
        byteCount = 1;
        res[0] = RES_PONG;
        break;

    case CMD_GETVER:
        byteCount = 4;
        res[0]    = version & 0xFF;
        res[1]    = (version & 0xFF00)               >> 8;;
        res[2]    = (version & 0xFF0000)             >> 16;;
        res[3]    = (version & 0xFF000000)           >> 24;;
        break;

    case CMD_GET_PARAMETER:
        byteCount = 1;
        res[0]    = parameter;
        break;

    case CMD_GET_RDY:
        byteCount = 1;
        //respond with 0 if something is in progress, 1 if ready, 2 is error
        if (setCalib || setTemperature || sleepOrWarmup) //if set calib or set Temperature is in progress, we are not ready
            res[0] = 0;
        else
            res[0]    = startConversion;
        break;

    case CMD_GET_CALIBRATED:
        byteCount = 1;
        if (calibrated) // we are already calibrated
            res[0] = 1;
        else
            res[0]    = 0;
        break;

    case CMD_GET_SENSOR_WAKEUP_TIME:
               byteCount = 2;
               res[0] = sensorWakeUpTime & 0xFF;
               res[1] = (sensorWakeUpTime >> 8) & 0xFF;
               break;

    case CMD_GET_FW_VERSION:
        byteCount = 1;
        res[0] = FW_VERSION;
        break;

    case CMD_GETVALUE1:
        byteCount = 8;
        res[0] =  values[0] & 0xFF;
        res[1] = (values[0] & 0xFF00)               >> 8;
        res[2] = (values[0] & 0xFF0000)             >> 16;
        res[3] = (values[0] & 0xFF000000)           >> 24;
        res[4] = (values[0] & 0xFF00000000)         >> 32;
        res[5] = (values[0] & 0xFF0000000000)       >> 40;
        res[6] = (values[0] & 0xFF000000000000)     >> 48;
        res[7] = (values[0] & 0xFF00000000000000)   >> 56;
        break;

    case CMD_GETVALUE2:
        byteCount = 8;
        res[0] =  values[1] & 0xFF;
        res[1] = (values[1] & 0xFF00)               >> 8;
        res[2] = (values[1] & 0xFF0000)             >> 16;
        res[3] = (values[1] & 0xFF000000)           >> 24;
        res[4] = (values[1] & 0xFF00000000)         >> 32;
        res[5] = (values[1] & 0xFF0000000000)       >> 40;
        res[6] = (values[1] & 0xFF000000000000)     >> 48;
        res[7] = (values[1] & 0xFF00000000000000)   >> 56;
        break;

    case CMD_GETRAWVALUE1:
        byteCount = 8;
        res[0] =  rawValues[0] & 0xFF;
        res[1] = (rawValues[0] & 0xFF00)               >> 8;
        res[2] = (rawValues[0] & 0xFF0000)             >> 16;
        res[3] = (rawValues[0] & 0xFF000000)           >> 24;
        res[4] = (rawValues[0] & 0xFF00000000)         >> 32;
        res[5] = (rawValues[0] & 0xFF0000000000)       >> 40;
        res[6] = (rawValues[0] & 0xFF000000000000)     >> 48;
        res[7] = (rawValues[0] & 0xFF00000000000000)   >> 56;
        break;

    case CMD_GETRAWVALUE2:
        byteCount = 8;
        res[0] =  rawValues[1] & 0xFF;
        res[1] = (rawValues[1] & 0xFF00)               >> 8;
        res[2] = (rawValues[1] & 0xFF0000)             >> 16;
        res[3] = (rawValues[1] & 0xFF000000)           >> 24;
        res[4] = (rawValues[1] & 0xFF00000000)         >> 32;
        res[5] = (rawValues[1] & 0xFF0000000000)       >> 40;
        res[6] = (rawValues[1] & 0xFF000000000000)     >> 48;
        res[7] = (rawValues[1] & 0xFF00000000000000)   >> 56;
        break;

    case CMD_CONVERT:
        startConversion = 0;
        break;

    case CMD_SET_TEMP:
        u.temp_array[0] = par[3];
        u.temp_array[1] = par[2];
        u.temp_array[2] = par[1];
        u.temp_array[3] = par[0];
        lastTemperature = u.float_variable*10; //float to centi grade
        setTemperature = true;
        break;

    case CMD_SET_CALIB:
        u.temp_array[0] = par[4];
        u.temp_array[1] = par[3];
        u.temp_array[2] = par[2];
        u.temp_array[3] = par[1];
        calibToSet = par[0];
        floatToSet = u.float_variable;
        setCalib = true;
        break;

    case CMD_SENSOR_WAKEUP:
        wakeUp = true;
        res[0] = RES_PONG;
        break;

    case CMD_SENSOR_SLEEP:
        goToSleep = true;
        res[0] = RES_PONG;
    break;

    case CMD_SOFTWARE_RESET:
        WDTCTL = 0xDEAD;
    break;


    case CMD_GET_SENSORVOLTAGE:
        byteCount = 1;

        #if SELECTED_SENSOR == 1
        res[0] = (1) | (0 << 1) | (0 << 2);

        #elif SELECTED_SENSOR == 2
        res[0] = (1) | (0 << 1) | (0 << 2);

        #elif SELECTED_SENSOR == 3
        res[0] = (1) | (0 << 1) | (0 << 2);

        #elif SELECTED_SENSOR == 4
       res[0] = (1) | (0 << 1) | (0 << 2);

        #elif SELECTED_SENSOR == 5
       res[0] = (1) | (0 << 1) | (0 << 2);

        #elif SELECTED_SENSOR == 6
        res[0] = (1) | (1 << 1) | (0 << 2);

        #endif

        break;

    default :
        res[0] = RES_ERROR;
    }
}

void start_cb()
{
    cmd = CMD_UNKNOWN;
    par[0] = PAR_UNKNOWN;
}

void receive_cb(unsigned char receive)
{
    //if command is still unknown, the byte should be a command
    if(cmd == CMD_UNKNOWN) {
        byteCount=1;
        //save command in cmd
        cmd = receive;

        //process one byte commands:
        if( cmd == CMD_GETVER       ||
            cmd == CMD_PING         ||
            cmd == CMD_GETVALUE1    ||
            cmd == CMD_GETVALUE2    ||
            cmd == CMD_GETRAWVALUE1    ||
            cmd == CMD_GETRAWVALUE2    ||
            cmd == CMD_CONVERT      ||
            cmd == CMD_GET_SENSORVOLTAGE ||
            cmd == CMD_SENSOR_WAKEUP ||
            cmd == CMD_SENSOR_SLEEP ||
            cmd == CMD_GET_PARAMETER ||
            cmd == CMD_GET_RDY      ||
            cmd == CMD_GET_CALIBRATED ||
            cmd == CMD_GET_SENSOR_WAKEUP_TIME ||
            cmd == CMD_GET_FW_VERSION ||
            cmd == CMD_SOFTWARE_RESET
            )
        {
            process_cmd(cmd, (uint8_t *)par);
        }
    //else - cmd is known
    }
    else
    {
        byteCount++;
        //byte is a parameter of the command
        //process 2 byte commands (1 byte command, 1 byte parameter)
        if (cmd == CMD_1ByteDummyTest)
        {
            par[0] = receive;
            process_cmd(cmd, (uint8_t *)par);
        }
        else if (cmd == CMD_SET_TEMP)
        {
            //process 5 byte commands (1 byte command, 4 byte parameter)
            if (byteCount==5)
            {
                par[3] = receive;
                process_cmd(cmd, (uint8_t *)par);
            }
            if (byteCount==4)
            {
                par[2] = receive;
            }
            if (byteCount==3)
            {
                par[1] = receive;
            }
            if (byteCount==2)
                par[0] = receive;
        }
        else if (cmd == CMD_SET_CALIB)
        {
            //process 6 byte commands (1 byte command, 5 byte parameter)
            if (byteCount==6)
            {
                par[4] = receive;
                process_cmd(cmd,(uint8_t *) par);
            }
            if (byteCount==5)
            {
                par[3] = receive;
            }
            if (byteCount==4)
            {
                par[2] = receive;
            }
            if (byteCount==3)
            {
                par[1] = receive;
            }
            if (byteCount==2)
                par[0] = receive;
        }
    }
}

void transmit_cb(unsigned char volatile *byte)
{
    if (byteCount>0)
    {
        byteCount--;
        *byte = res[byteCount];
    }
    else
        *byte = RES_ERROR;
}
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

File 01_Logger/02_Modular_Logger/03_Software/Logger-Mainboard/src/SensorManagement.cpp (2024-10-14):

/*
 * CopyrightText: (C) 2024 Hensel Elektronik GmbH
 *
 * License-Identifier: MPL-2.0
 *
 * Project: Hydrography on Fishing Vessels
 * Project URL: <https://github.com/HyFiVeUser/HyFiVe>, <https://hyfive.info>
 *
 * Description: Sensor management and data collection
 */

#include <ArduinoJson.h>
#include <atomic>
#include <iomanip>

#include "BMS.h"
#include "Charger.h"
#include "DS3231TimeNtp.h"
#include "DebuggingSDLog.h"
#include "DeepSleep.h"
#include "Led.h"
#include "LoggerHER.h"
#include "MQTTManager.h"
#include "SDCard.h"
#include "SensorManagement.h"
#include "SystemVariables.h"
#include "Utility.h"
#include "WifiNetwork.h"
#include "loggerConfig.h"
#include "loggerConfigValidation.h"
#include "sample_cast.h"

int64_t AdapterSensorRawValue[MAX_SENSOR_CREDENTIALS];
uint8_t AdapterSensorTypeID[MAX_SENSOR_CREDENTIALS];
uint8_t AdapterConfig_Value_Type[MAX_SENSOR_CREDENTIALS];
int64_t AdapterSensorCalcValue[MAX_SENSOR_CREDENTIALS];
uint32_t bootCount = 0;
uint8_t MAX_NUM_SENSORS = MAX_SENSOR_CREDENTIALS;

TwoWire i2cBus(0);
SPIClass *spi_interface;
#define SD_CS 18
#define SDA_PIN 4
#define SCL_PIN 5

bool measurementSuccessful[MAX_SENSOR_CREDENTIALS];
float sensorValue[MAX_SENSOR_CREDENTIALS];
float sensorValueRaw[MAX_SENSOR_CREDENTIALS];

/**
 * @brief Initializes the logger.
 */
void initializeLogger()
{
  if (!isFirstBoot)
  {
    delay(5000); // at least 5 seconds are required for initialization when the interface board is started for the first time
  }

  Logger.Init(i2cBus,
              AdapterSensorTypeID,
              AdapterConfig_Value_Type,
              AdapterSensorRawValue,
              AdapterSensorCalcValue,
              bootCount,
              ((int)SD_CS),
              ((int)SDA_PIN),
              ((int)SCL_PIN),
              spi_interface);

  for (int i = 0; i < MAX_NUM_SENSORS; i++)
  {
    AdapterSensorRawValue[i] = 0;
    AdapterSensorCalcValue[i] = 0;
  }

  Logger.begin_I2C();
}

/**
 * @brief Converts a uint32_t to float using IEEE-754 Floating Point conversion.
 * @param decimalValue The uint32_t value to convert.
 * @return float The converted float value.
 */
float floatingPointConvert(uint32_t decimalValue)
{
  union
  {
    uint32_t i;
    float f;
  } converter;

  converter.i = decimalValue;
  return converter.f;
}

void addSensorToErrorSkip(int sensorNumber)
{
  // Check whether the sensor is already in the list
  for (int i = 0; i < errorSkipSensorSize; i++)
  {
    if (errorSkipSensor[i] == sensorNumber)
    {
      return; // Sensor is already in the list, nothing to do
    }
  }

  // Add the sensor to the list if there is still space
  if (errorSkipSensorSize < MAX_SENSOR_CREDENTIALS)
  {
    errorSkipSensor[errorSkipSensorSize++] = sensorNumber;
    Log(LogCategorySensors, LogLevelERROR, "sensor_id ", String(configRTC.sensor[sensorNumber].sensor_id), " added to errorSkipSensor");
  }
  else
  {
    Log(LogCategorySensors, LogLevelERROR, "errorSkipSensor is full, cannot add sensor ", String(sensorNumber));
  }
}

void detectConnecteOxygenSensor(uint8_t sensorNumber)
{
  for (int i = 0; i < errorSkipSensorSize; i++)
  {
    if (temperatureSensorBusAddress == configRTC.sensor[errorSkipSensor[i]].bus_address)
    {
      addSensorToErrorSkip(sensorNumber);
      return;
    }
  }

  if (oxygenSensorBusAddress != 255 && temperatureSensorBusAddress != 255)
  {
    for (int x = 0; x < 100; x++)
    {
      Logger.getInterfaceRDY(temperatureSensorBusAddress);
      uint32_t interfaceRDY = AdapterSensorRawValue[temperatureSensorBusAddress];

      if (interfaceRDY == 1)
      {
        break;
      }
      delay(10);
    }

    Logger.Measure(temperatureSensorBusAddress, temperatureSensorParameter);
    uint32_t rawValue = AdapterSensorRawValue[temperatureSensorBusAddress];
    float sensorValueTemp = floatingPointConvert(rawValue);
    Log(LogCategorySensors, LogLevelDEBUG, "sensorValueTemp: ", String(sensorValueTemp));
    setSensorTempToInterface(oxygenSensorBusAddress, sensorValueTemp);
  }
}
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

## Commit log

2024-08-08 initial commit
    Initial commit of the HyFiVe project
    [BOM.xlsx, BOM_otterboard_mounting.xlsx, Calculation_Wall_Thickness.xlsx, DeckunitV1 v1.stl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]
2024-09-06 Add modular logger files and change structure accordingly
    [Analog-Adapter.kicad_pcb, Analog-Adapter.kicad_sch, BOM.xlsx, BOM_otterboard_mounting.xlsx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]
2024-09-17 edited logger readmes and added pictures
    [BOM.xlsx]
2024-09-20 readmes updated (config update of logger, sensors and deckbox)
    [logger_config_parameters.xlsx]
2024-09-23 updated readmes (deckbox; introducing bi-directional communication)
    [BOM.xlsx, logger_config_parameters.xlsx]
2024-09-24 updated readmes (server)
    [logger_config_parameters.xlsx]
2024-09-26 additional CAD-Files
    Adding F3D, STEP and PNG-Files for all relevant mechanical parts.
    [Deckbox_mounting_antennas_all_levels.f3z, Deckbox_mounting_antennas_level_1.step, Deckbox_mounting_antennas_level_2.step, Deckbox_mounting_antennas_level_3.ste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]
2024-10-11 update Electronics for Modular_Logger
    [Battery_Charger.kicad_sch, HyFiVe-BOM_Adapter.ods, HyFiVe-BOM_Main_Unit.ods, MPU.kicad_sch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]
2024-10-11 folder structure adjusted
    [Analog-Adapter.kicad_pcb, Analog-Adapter.kicad_sch, Battery_Charger.kicad_sch, HyFiVe-BOM_Adapter.ods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]
2024-10-14 Assembly Instructions 02_Modular_Logger
2024-11-07 firmware update V0.7
    Previously, if the battery was discharged below 5%, errors occurred during charging due to undervoltage
    This issue has been resolved with the current firmware update
2024-11-11 Charging process adjusted up to 100%, as battery-dependent variations are possible
    FW: 0.71
2024-11-20 added OTA (Over-The-Air) firmware update feature
    Firmware Update v0.80
    - Added OTA firmware update feature
    - Enhanced code comments
    - Optimized function behavior
    - Implemented Node-RED flow for OTA firmware updates (nodered_all_flows_20241120.json)
2025-02-04 Update DeckunitV1_BOM.csv
    Some parts were replaced by better available equivalent parts from other manufacturers
    [DeckunitV1_BOM.csv]
2025-07-07 Update README.md
    Update instruction for assembly of deckbox 2.0
2025-07-08 added images
    added images for mounting antennas
2025-07-11 Update README.md
    mounting antenna
2025-07-18 new picturs and updated holes drawing
2025-07-22 add instructions for raspi case
2025-07-23 general alarm time update
    [LED_signals_rev1_1.xlsx]
2025-07-23 typos, new images for pcb connection
2025-07-23 new images for pcb connection
2025-07-25 update BOM.xlsx to content of readme.md
    [BOM.xlsx]
2025-07-25 CAD-Files updated
    Updated all CAD files to new Deckbox Version
    [AC_DC_housing_v2.step, AC_DC_housing_v2.stl, DC_DC_Clamp_v2.step, DC_DC_Clamp_v2.stl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]
2025-07-25 add wiring diagram
2025-07-25 Deckbox Upgrade 2.0 to IP67 (#2)
    * Update README.md
    * added images for updated instructions
    * Update BOM and Tools
    * intructions for USB and Molex Plug
    Updated BOM.xlsx
    Deleted old images
    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
    [AC_DC_housing_v2.step, AC_DC_housing_v2.stl, BOM.xlsx, DC_DC_Clamp_v2.step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]

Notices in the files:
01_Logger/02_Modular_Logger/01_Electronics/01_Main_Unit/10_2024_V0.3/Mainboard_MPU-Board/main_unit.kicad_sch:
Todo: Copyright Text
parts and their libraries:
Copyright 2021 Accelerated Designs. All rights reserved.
